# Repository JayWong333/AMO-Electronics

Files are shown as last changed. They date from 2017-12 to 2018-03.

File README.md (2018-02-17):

# AMO-Electronics
Collection of electronics projects intended for conducting atomic physics experiments.

## ECDL_CUR_CTRL
This folder contains the schematics and board layout for an ultra-low noise laser diode current controller. It builds upon proven designs of Libbrecht & Hall (https://doi.org/10.1063/1.1143949) as well as Erickson et. al. (https://doi.org/10.1063/1.2953597).

## Analog Temp Controller
This folder contains the schematics and board layout for a thermoelectric cooler controller. It features a PID-loop that drives a Peltier element (or alternatively a resistive heater) in order to match the resistance of a NTC thermistor to a given set temperature.

## Pfeiffer Compact Gauge Controller
A small standalone board which can be used to interface the Pfeiffer PKR/IKR series compact vacuum gauges. Features an ATMEGA32U4 microcontroller to convert the measurement signal to a pressure and provide it via the built-in USB interface or a I2C/SPI display. The accompanying firmware (in form of an Arduino sketch) can be found in the FW folder.

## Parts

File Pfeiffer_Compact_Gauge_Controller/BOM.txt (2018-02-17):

Partlist exported from C:/Users/alexi/OneDrive/MOTATHOME/780nm Laser Source/AMO-Electronics/Pfeiffer_Compact_Gauge_Controller/Pfeiffer_Compact_Gauge_Controller.sch at 1/28/2018 9:25 PM

Qty Value              Device                                       Package                  Parts                              Description                          CASE MONTHLY_USAGE MPN           OC_FARNELL OC_NEWARK PACKAGE PART_NUMBER                  PRICE PROD_ID    SF_SKU    SPICEPREFIX SUPPLIER               TYPE       VALUE             
1                      DB9MALE                                      DB9_MALE                 J1                                 DB9 Connector                                                                                                                         CONN-09904                                                                           
1                      KX-7                                         3.2X2.5_KX-7             X1                                 Quartz Crystals (MHz) SMD:                                                                                                                                                                                                 
1                      LEDCHIPLED_0805                              CHIPLED_0805             5V                                 LED                                                                                                                                                                                                                        
1                      PINHD-1X2                                    1X02                     JP7                                PIN HEADER                                                                                                                                                                                                                 
1                      PINHD-1X2/90                                 1X02/90                  JP1                                PIN HEADER                                                                                                                                                                                                                 
3                      PINHD-2X2                                    2X02                     JP2, JP4, JP5                      PIN HEADER                                                                                                                                                                                                                 
1                      PINHD-2X3                                    2X03                     JP6                                PIN HEADER                                                                                                                                                                                                                 
1                      PINHD-2X4                                    2X04                     JP3                                PIN HEADER                                                                                                                                                                                                                 
1                      USBMINIB                                     USB-MINIB                USB                                USB Connectors                                                                                                                                                                                                             
6   0.1uF              C-EUC0805                                    C0805                    C5, C6, C7, C8, C9, C10            CAPACITOR, European symbol                                                                                                                                 C                                                               
1   0R                 R-US_R0805                                   R0805                    R9                                 RESISTOR, American symbol                                                                                                                                  R                                                               
1   100K               R-US_R0805                                   R0805                    R1                                 RESISTOR, American symbol                                                                                                                                  R                                                               
1   100nF              C-EUC0805                                    C0805                    C12                                CAPACITOR, European symbol                                                                                                                                 C                                                               
8   10K                R-US_R0805                                   R0805                    R2, R5, R6, R8, R10, R11, R12, R59 RESISTOR, American symbol                                                                                                                                  R                                                               
1   10nF               C-EUC0805                                    C0805                    C14                                CAPACITOR, European symbol                                                                                                                                 C                                                               
3   10uF               C-EUC0805                                    C0805                    C15, C16, C17                      CAPACITOR, European symbol                                                                                                                                 C                                                               
1   11K                R-US_R0805                                   R0805                    R7                                 RESISTOR, American symbol                                                                                                                                  R                                                               
1   1A/40V/500mV       DIODE-SCHOTTKY-SS14                          SMA-DIODE                D1                                 Schottky diode                                                                                                                        DIO-08053                                                          1A/40V/500mV      
3   1uF                C-EUC0805                                    C0805                    C3, C4, C11                        CAPACITOR, European symbol                                                                                                                                 C                                                               
2   22R                R-US_R0805                                   R0805                    R3, R4                             RESISTOR, American symbol                                                                                                                                  R                                                               
2   22pF               C-EUC0805                                    C0805                    C1, C2                             CAPACITOR, European symbol                                                                                                                                 C                                                               
1   22uF               CP_SV-C                                      CSV-C                    C13                                POLARIZED CAP                                                                                                                                                                                                              
1   2K                 R-US_R0805                                   R0805                    R13                                RESISTOR, American symbol                                                                                                                                  R                                                               
1   ATMEGA32U4-AU      ATMEGA32U4-AU                                TQFP44                   U1                                 http://www.ladyada.net/library/eagle                                                                                                                                                                                       
1   LM340A             LM1117IMP-5.0                                SOT230P696X180-4N        U6                                 IC REG LDO 800MA 5.0V                                   LM1117IMP-5.0 -          41K3451   SOT-223                                                                     National Semiconductor                              
1   MF-MSMF050-2 500mA PROTEZIONE_0002_MF-MSMF050-2                 PROTEZIONE_L1812         F1                                 500 mA Multifuse ? Polyfuse               _____                                                    MF-MSMF050-2                 _____                                  _____                  Protezione MF-MSMF050-2 500mA
1   MH2029-300Y        PROTEZIONE_0001_BLM21PG300SN1D_/_MH2029-300Y PROTEZIONE_0805          L4                                 BLM21                                     _____                                                    BLM21PG300SN1D_/_MH2029-300Y _____                                  _____                  Protezione MH2029-300Y       
1   MOM SWITCH         MOMENTARY-SWITCH-SPST-SMD-5.2MM              TACTILE_SWITCH_SMD_5.2MM S1                                 Momentary Switch (Pushbutton) - SPST                                                                                                  SWCH-08247 COM-08720                                                                 
4   MOUNT-PAD-ROUND2.8 MOUNT-PAD-ROUND2.8                           2,8-PAD                  H1, H2, H3, H4                     MOUNTING PAD, round                                                                                                                                                                                                        
1   OPEN               R-US_R0805                                   R0805                    R14                                RESISTOR, American symbol                                                                                                                                  R                                                               
1   TL072D             TL072D                                       SO08                     IC1                                OP AMP

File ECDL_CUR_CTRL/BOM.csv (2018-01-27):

Qty | Value | Device | Package | Got
2 |  | LEDCHIPLED_0805 | CHIPLED_0805 | x
1 |  | MMBT2907ALT1-PNP-SOT23-BEC | SOT23-BEC | x
3 |  | PINHD-1X2 | 1X02 | o
1 |  | PINHD-1X2/90 | 1X02/90 | o
1 |  | PINHD-1X3 | 1X03 | o
1 |  | PINHD-1X3/90 | 1X03/90 | o
1 |  | PINHD-1X5 | 1X05 | o
1 |  | PINHD-2X3 | 2X03 | o
1 |  | PINHD-2X4 | 2X04 | o
3 |  | SMACONNECTOR | SMA90_DIP | x
4 |  | TEST-POINT2 | PAD.02X.02 | x
1 |  | USBMINIB | USB-MINIB | x
1 | .01uF | C-EUC0805 | C0805 | x
2 | 0.1uF | C-EUC0805 | C0805 | x
3 | 0R | R-US_R0805 | R0805 | x
1 | 1.5R | R-US_R2512 | R2512 | x
5 | 100K | R-US_R0805 | R0805 | x
1 | 100R | R-US_R0805 | R0805 | x
2 | 100R | R-US_R2512 | R2512 | x
22 | 100nF | C-EUC0805 | C0805 | x
1 | 100uH | CD54 | CD54 | o
38 | 10K | R-US_R0805 | R0805 | x
3 | 10nF | C-EUC0805 | C0805 | x
16 | 10uF | C-EUC0805 | C0805 | x
1 | 11K | R-US_R0805 | R0805 | x
8 | 1K | R-US_R0805 | R0805 | x
2 | 1N4001 | MBRA340T3 | SMA | x
6 | 1uF | C-EUC0805 | C0805 | x
2 | 220uF | CP_SV-D | CSV-D | x
1 | 22uF | C-EUC0805 | C0805 | x
2 | 22uF | CP_SV-C | CSV-C | x
1 | 240R | R-US_R0805 | R0805 | x
1 | 28.7K | R-US_R0805 | R0805 | x
3 | 2K | R-US_R0805 | R0805 | x
1 | 2N7002 | SMD-MOSFET-N-CH-60V-300MA-LOGIC-LEVEL-FET-2N7002(SOT-23) | SOT-23 | x
1 | 32.768Khz_SMD | CRISTALLI_0213_ABS07-32.768KHZ-T | EPSON_FC_145 | x
2 | 330R | R-US_R0805 | R0805 | x
1 | 33nF | C-EUC0805 | C0805 | x
1 | 3A/40V/500mV | DIODE-SCHOTTKY-B340A | SMA-DIODE | x
2 | 3K | R-US_R0805 | R0805 | x
2 | 47uF | CP_3528-21R | C3528-21R/T | x
1 | 50K | R-US_R0805 | R0805 | x
1 | 50R | R-US_R0805 | R0805 | x
1 | 50R or 0R | R-US_R0805 | R0805 | x
1 | 5K | R-TRIMM3296W | RTRIM3296W | x
1 | 7.5K | R-US_R0805 | R0805 | x
1 | 74LVC1G125DCKR | SN74LVC1G125DCKR | SC70-5 | x
1 | AD5541 | AD5541 | SOIC-8 | x
2 | AD8676 | AD8676 | SO8 | x
1 | ATSAMD21G-A | ATSAMD21G-A | TQFP-48 |  | <<
2 | BRNCG0603MLC-05E | BRNCG0603MLC-05E | CT/CN0603 | x
2 | CD54 | CD54 | CD54 | x
1 | ENBL | PINHD-1X2 | 1X02 | o
1 | EN_LED | PINHD-1X2 | 1X02 | o
1 | IRF9Z14 | IRF9530 | TO220BV | x
1 | L7912 | L7912 | TO223-3 | x
1 | LM1117IMP-3.3 | LM1117IMP-3.3 | SOT230P696X180-4N | x
1 | LM1117IMP-5.0 | LM1117IMP-5.0 | SOT230P696X180-4N | x
1 | LM317MDT | LM317MDT | DPACK | x
1 | LM340S-12 | LM340S-12 | TO263-3 | x
1 | LM399H | LM399H | TO39/4 | x
1 | MF-MSMF050-2 500mA | MF-MSMF050-2 | L1812 | x
1 | MH2029-300Y | BLM21PG300SN1D_/_MH2029-300Y | 805 | x
1 | MOM SWITCH | MOMENTARY-SWITCH-SPST-SMD-5.2MM | SWITCH_SMD_5.2MM | x
1 | OPA2227D | OPA2227D | SO08 |  | <<
1 | PMV48XP | TRANSISTORS_0297_PMV48XP | TRANSISTORS_SOT-23 | x
1 | SSM3J328R.LF | SMD-MOSFET-P-CH-20V-6A-SSM3J328R(SOT-23) | SOT-23 | x
1 | TL071D | TL071D | SO08 | x
1 | TS514AID | TS514AID | SOIC127P600X175-14N | x

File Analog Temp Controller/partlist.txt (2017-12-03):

Partlist

Exported from ECDL_CUR_CTRL.brd at 9/26/2017 2:15 PM

EAGLE Version 8.3.1 Copyright (c) 1988-2017 Autodesk, Inc.

Assembly variant: 

Part     Value          Package            Library                                Position (mil)        Orientation

C11      C_SNUB         C0603              rcl                                    (2050 530)            R270
R9       R_SNUB         R0603              rcl                                    (2050 400)            R90

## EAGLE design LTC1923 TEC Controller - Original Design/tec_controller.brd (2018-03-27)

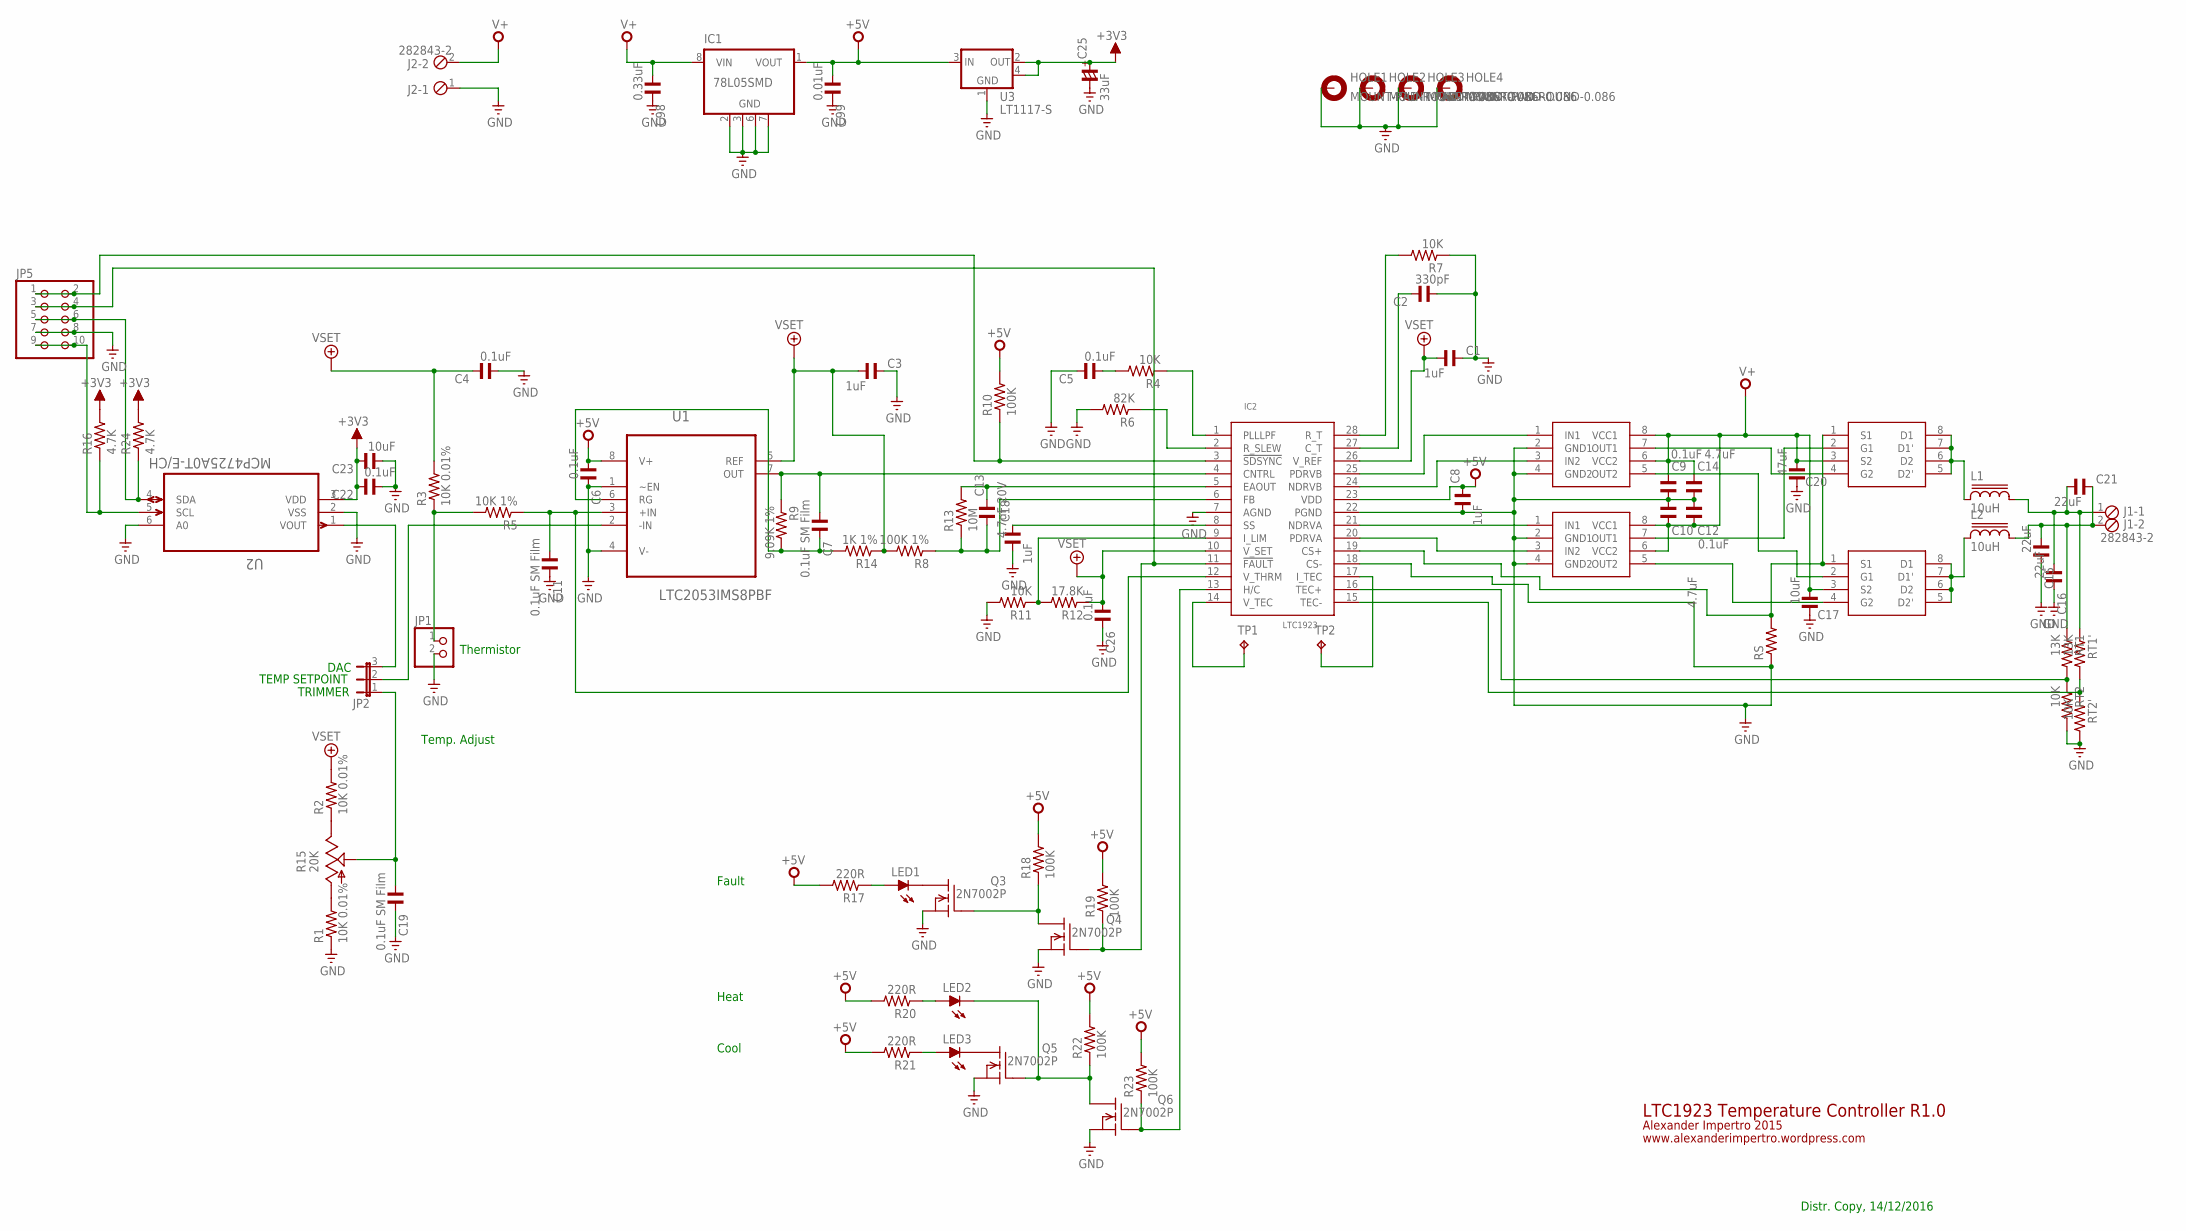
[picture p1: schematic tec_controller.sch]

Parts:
C1, C3, C8, C18: 1uF; C0603
C2: 330pF; C0603
C4, C5, C6, C9, C12, C22, C26: 0.1uF; C0603
C7, C11, C19: 0.1uF SM Film; C0805
C10, C14: 4.7uF; C0603
C13: 4.7uF 20V; C1206
C15, C16, C21: 22uF; C0603
C17, C23: 10uF; C0603
C20: 47uF; C0805
C25: 33uF; 153CLV-0505
C98: 0.33uF; C0805
C99: 0.01uF; C0805
HOLE1, HOLE2, HOLE3, HOLE4: MOUNT-PAD-ROUND-0.086; 086-PAD
IC1: 78L05SMD; SO08
IC2: LTC1923; SSOP28
IC3, IC4: LTC1693-1; SO-08
IC5, IC6: IRF7343; SO-08
J1, J2: 282843-2
JP1: PINHD-1X2; 1X02
JP2: JP2E; JP2
JP5: PINHD-2X5; 2X05
L1, L2: 10uH; DRA127
LED1, LED2, LED3: LEDCHIPLED_0805; CHIPLED_0805
Q3, Q4, Q5, Q6: 2N7002P; SOT95P230X110-3N
R1, R2, R3: 10K 0.01%; R0603
R4, R7, R11: 10K; R0603
R5: 10K 1%; R0603
R6: 82K; R0603
R8: 100K 1%; R0603
R9: 9.09K 1%; R0603
R10: 100K; R0805
R12: 17.8K; R0805
R13: 10M; R0805
R14: 1K 1%; R0603
R15: 20K; B25P
R16, R24: 4.7K; R0603
R17, R20, R21: 220R; R0603
R18, R19, R22, R23: 100K; R0603
RS: R-EU_R2512; R2512
RT1, RT1': 13K; R0603
RT2, RT2': 10K; R0603
TP1, TP2: TPTP10SQ; TP10SQ
U1: LTC2053IMS8PBF; SOP65P490X110-8N
U2: MCP4725A0T-E/CH; SOT95P270X145-6N
U3: LT1117-S; SOT223

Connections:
+3V3: C22.1, C23.1, C25.+, R16.2, R24.2, U2.3 (VDD), U3.2 (OUT), U3.4 (TAB)
+5V: C6.2, C8.1, C99.2, IC1.1 (VOUT), IC2.23 (VDD), R10.2, R17.2, R18.2, R19.2, R20.2, R21.2, R22.2, R23.2, U1.8 (V+), U3.3 (IN)
+5V/2: C1.2, C3.2, C4.1, C26.2, IC2.10 (V_SET), IC2.26 (V_REF), R2.2, R3.2, R8.2, R12.1, R14.1, U1.5 (REF)
GND: C1.1, C2.2, C3.1, C4.2, C5.1, C6.1, C8.2, C9.1, C10.2, C11.1, C12.2, C14.1, C15.1, C16.1, C17.1, C18.2, C19.1, C20.1, C22.2, C23.2, C25.-, C26.1, C98.1, C99.1, HOLE1.B086, HOLE2.B086, HOLE3.B086, HOLE4.B086, IC1.2 (GND), IC1.3 (GND), IC1.6 (GND), IC1.7 (GND), IC2.7 (AGND), IC2.18 (CS-), IC2.22 (PGND), IC3.2 (GND1), IC3.4 (GND2), IC4.2 (GND1), IC4.4 (GND2), J2.1, JP1.2, JP5.7, JP5.8, Q3.2 (S), Q4.2 (S), Q5.2 (S), Q6.2 (S), R1.1, R6.2, R7.1, R11.2, RS.1, RT2.2, RT2'.2, U1.1 (~EN), U1.4 (V-), U2.2 (VSS), U2.6 (A0), U3.1 (GND)
unnamed: LED2.C, Q5.1 (G), Q6.3 (D), R22.1
unnamed: C2.1, IC2.27 (C_T)
unnamed: IC2.14 (V_TEC), TP1.TP
unnamed: IC2.17 (I_TEC), TP2.TP
unnamed: IC2.13 (H/C), Q6.1 (G), R23.1
unnamed: IC2.28 (R_T), R7.2
unnamed: LED3.C, Q5.3 (D)
unnamed: LED2.A, R20.1
unnamed: LED3.A, R21.1
unnamed: IC2.11 (!FAULT), JP5.3, JP5.4, Q4.1 (G), R19.1
unnamed: Q3.1 (G), Q4.3 (D), R18.1
unnamed: LED1.C, Q3.3 (D)
unnamed: LED1.A, R17.1
unnamed: C7.2, IC2.4 (CNTRL), R9.1, U1.7 (OUT)
unnamed: C11.2, IC2.12 (V_THRM), R5.1, U1.3 (+IN)
unnamed: JP1.1, R3.1, R5.2
unnamed: C7.1, R9.2, R14.2, U1.6 (RG)
unnamed: JP2.2, U1.2 (-IN)
unnamed: R1.2, R15.A
unnamed: R2.1, R15.E
unnamed: IC2.9 (I_LIM), R11.1, R12.2
unnamed: IC2.2 (R_SLEW), R6.1
unnamed: JP2.3, U2.1 (VOUT)
unnamed: C18.1, IC2.8 (SS)
unnamed: C5.2, R4.2
unnamed: IC2.1 (PLLLPF), R4.1
unnamed: C13.2, IC2.6 (FB), R8.1, R13.1
unnamed: C13.1, IC2.5 (EAOUT), R13.2
unnamed: C19.2, JP2.1, R15.S
unnamed: IC2.16 (TEC+), RT1.2, RT2.1
unnamed: IC2.25 (PDRVB), IC3.1 (IN1)
unnamed: IC2.24 (NDRVB), IC3.3 (IN2)
unnamed: IC2.21 (NDRVA), IC4.1 (IN1)
unnamed: IC2.20 (PDRVA), IC4.3 (IN2)
unnamed: IC2.15 (TEC-), RT1'.2, RT2'.1
unnamed: IC2.3 (!SDSYNC), JP5.1, JP5.2, R10.1
unnamed: IC2.19 (CS+), IC5.1 (S1), IC6.1 (S1), RS.2
unnamed: IC4.7 (OUT1), IC5.2 (G1)
unnamed: IC3.7 (OUT1), IC5.4 (G2)
unnamed: IC3.5 (OUT2), IC6.2 (G1)
unnamed: C16.2, C21.2, J1.1, L1.2, RT1'.1
unnamed: C15.2, C21.1, J1.2, L2.2, RT1.1
unnamed: IC5.5 (D2'), IC5.6 (D2), IC5.7 (D1'), IC5.8 (D1), L1.1
unnamed: IC6.5 (D2'), IC6.6 (D2), IC6.7 (D1'), IC6.8 (D1), L2.1
unnamed: JP5.5, JP5.6, R24.1, U2.4 (SDA)
unnamed: JP5.9, JP5.10, R16.1, U2.5 (SCL)
unnamed: IC4.5 (OUT2), IC6.4 (G2)
V+: C9.2, C10.1, C12.1, C14.2, C17.2, C20.2, C98.2, IC1.8 (VIN), IC3.6 (VCC2), IC3.8 (VCC1), IC4.6 (VCC2), IC4.8 (VCC1), IC5.3 (S2), IC6.3 (S2), J2.2

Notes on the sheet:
Cool
Heat
Fault
Thermistor
Temp. Adjust
TEMP SETPOINT
DAC
TRIMMER
Alexander Impertro 2015
www.alexanderimpertro.wordpress.com
LTC1923 Temperature Controller R1.0
Distr. Copy, 14/12/2016

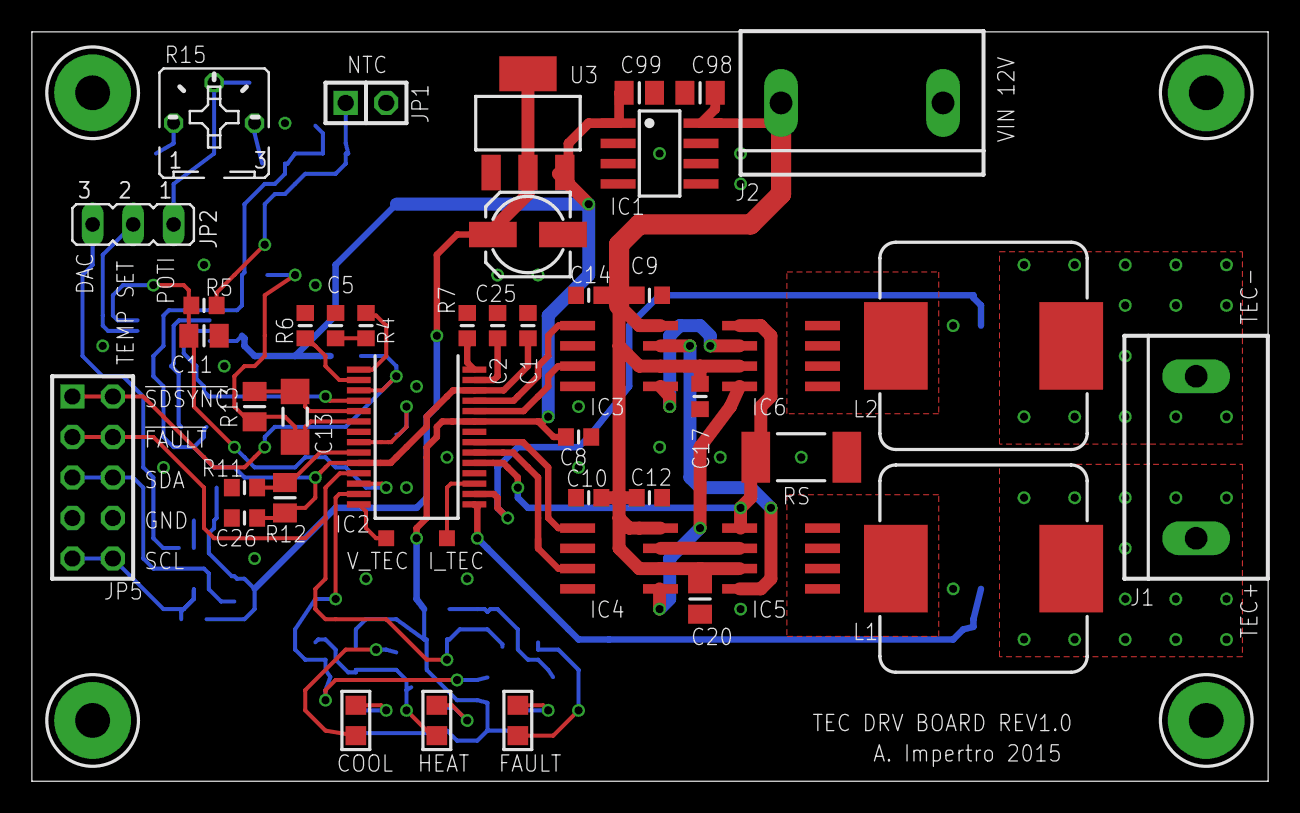
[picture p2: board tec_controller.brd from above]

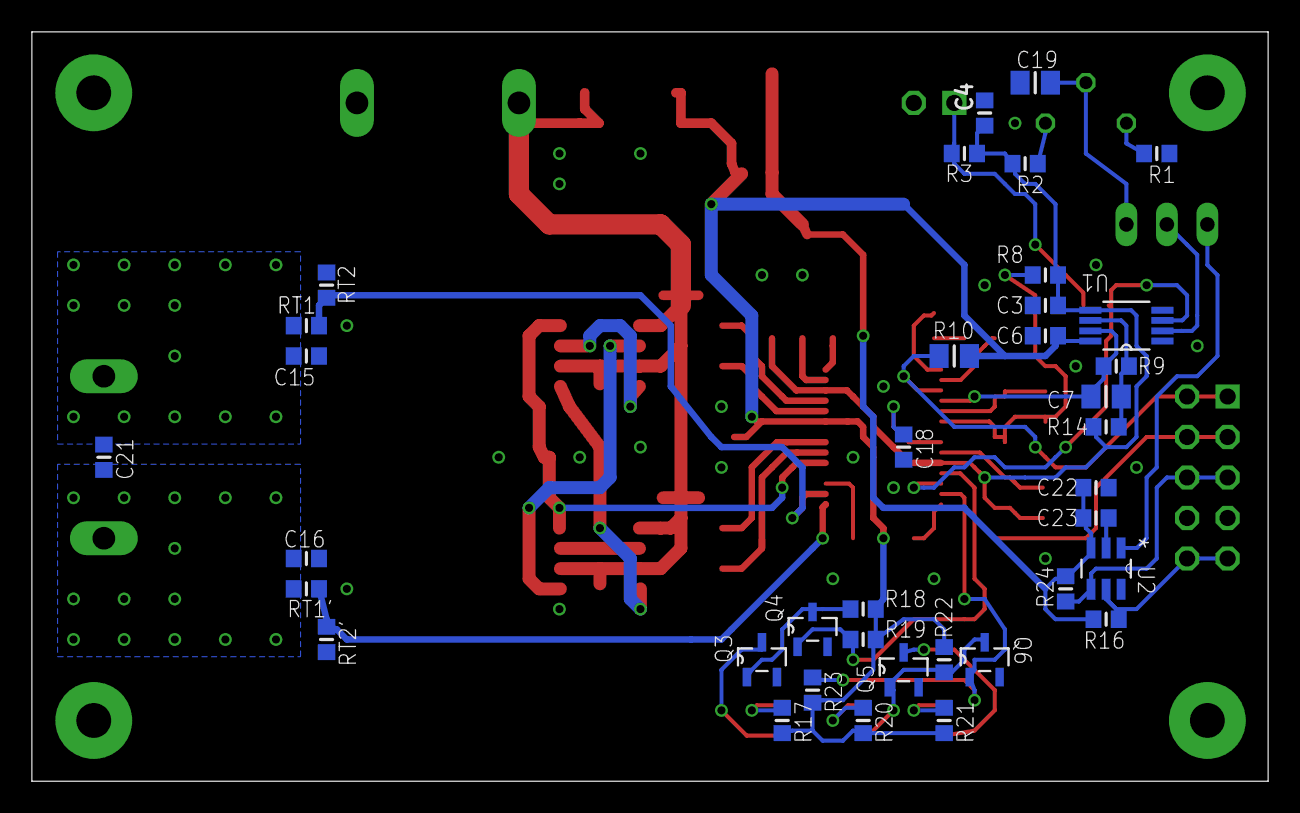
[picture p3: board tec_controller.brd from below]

Board: 2 copper layers, 77.5 x 47.0 mm, 85 parts (37 on the bottom side), 52 nets.

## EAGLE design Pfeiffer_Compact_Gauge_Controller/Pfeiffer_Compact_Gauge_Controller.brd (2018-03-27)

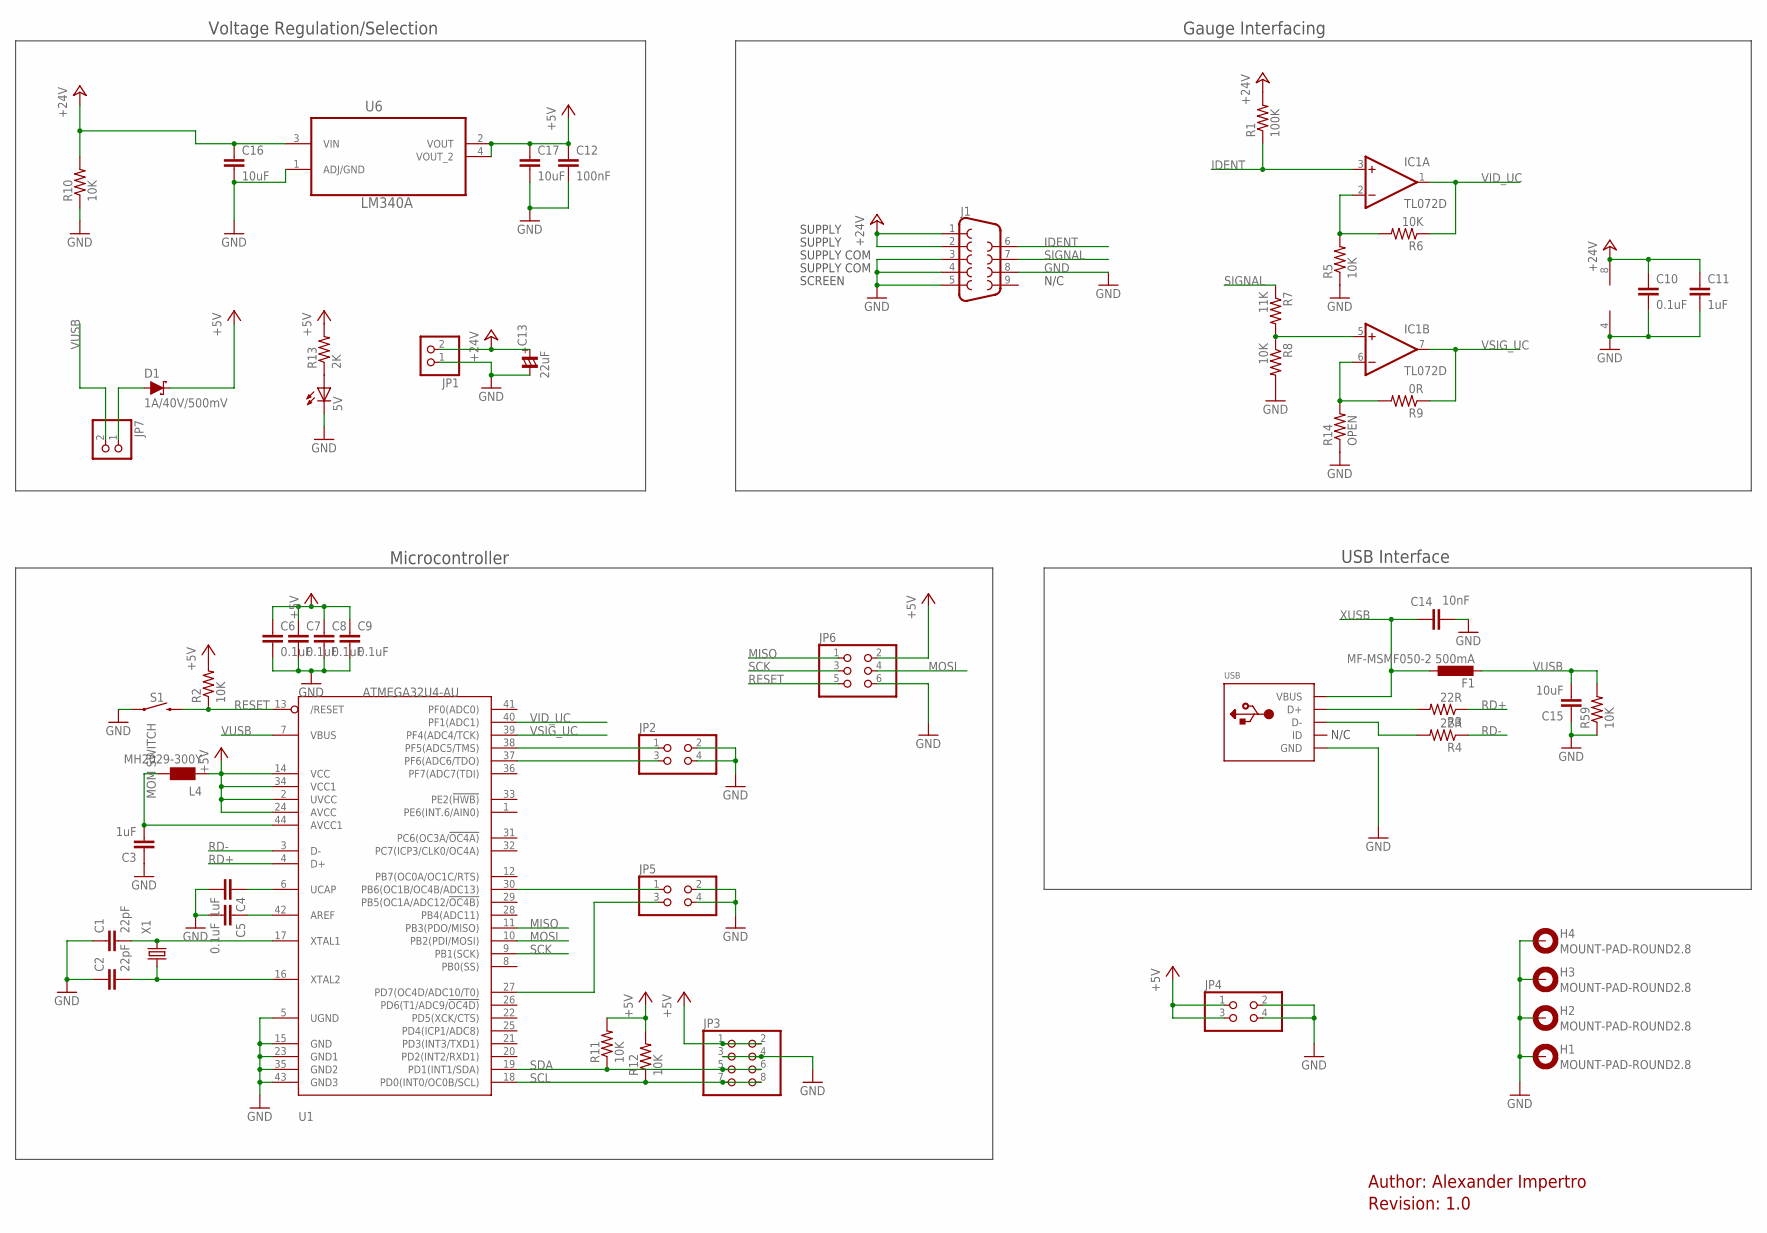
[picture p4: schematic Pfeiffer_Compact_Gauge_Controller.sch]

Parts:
5V: LEDCHIPLED_0805; CHIPLED_0805
C1, C2: 22pF; C0805
C3, C4, C11: 1uF; C0805
C5, C6, C7, C8, C9, C10: 0.1uF; C0805
C12: 100nF; C0805
C13: 22uF; CSV-C
C14: 10nF; C0805
C15, C16, C17: 10uF; C0805
D1: 1A/40V/500mV; SMA-DIODE
F1: MF-MSMF050-2 500mA; PROTEZIONE_L1812
H1, H2, H3, H4: MOUNT-PAD-ROUND2.8; 2,8-PAD
IC1: TL072D; SO08
J1: DB9MALE; DB9_MALE
JP1: PINHD-1X2/90; 1X02/90
JP2, JP4, JP5: PINHD-2X2; 2X02
JP3: PINHD-2X4; 2X04
JP6: PINHD-2X3; 2X03
JP7: PINHD-1X2; 1X02
L4: MH2029-300Y; PROTEZIONE_0805
R1: 100K; R0805
R2, R5, R6, R8, R10, R11, R12, R59: 10K; R0805
R3, R4: 22R; R0805
R7: 11K; R0805
R9: 0R; R0805
R13: 2K; R0805
R14: OPEN; R0805
S1: MOM SWITCH; TACTILE_SWITCH_SMD_5.2MM
U1: ATMEGA32U4-AU; TQFP44
U6: LM340A; SOT230P696X180-4N
USB: USBMINIB; USB-MINIB
X1: KX-7; 3.2X2.5_KX-7

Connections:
+5V: C6.1, C7.1, C8.1, C9.1, C12.1, C17.1, D1.C, JP3.1, JP3.2, JP4.1, JP4.3, JP6.2, L4.1, R2.2, R11.2, R12.2, R13.2, U1.2 (UVCC), U1.14 (VCC), U1.24 (AVCC), U1.34 (VCC1), U6.2 (VOUT), U6.4 (VOUT_2)
+24V: C10.1, C11.1, C13.+, C16.1, IC1.8 (V+), J1.1, J1.2, JP1.2, R1.2, R10.2, U6.3 (VIN)
GND: 5V.C, C1.1, C2.1, C3.1, C4.2, C5.2, C6.2, C7.2, C8.2, C9.2, C10.2, C11.2, C12.2, C13.-, C14.2, C15.1, C16.2, C17.2, H1.B2,8, H2.B2,8, H3.B2,8, H4.B2,8, IC1.4 (V-), J1.3, J1.4, J1.5, J1.8, JP1.1, JP2.2, JP2.4, JP3.3, JP3.4, JP4.2, JP4.4, JP5.2, JP5.4, JP6.6, R5.1, R8.2, R10.1, R14.1, R59.1, S1.1, U1.5 (UGND), U1.15 (GND), U1.23 (GND1), U1.35 (GND2), U1.43 (GND3), U6.1 (ADJ/GND), USB.GND
IDENT: IC1.3 (+IN), J1.6, R1.1
MISO: JP6.1, U1.11 (PB3(PDO/MISO))
MOSI: JP6.4, U1.10 (PB2(PDI/MOSI))
unnamed: C1.2, U1.17 (XTAL1), X1.3 (2)
unnamed: C2.2, U1.16 (XTAL2), X1.1
unnamed: C3.2, L4.2, U1.44 (AVCC1)
unnamed: C4.1, U1.6 (UCAP)
unnamed: C5.1, U1.42 (AREF)
unnamed: R3.2, USB.D+
unnamed: R4.2, USB.D-
unnamed: IC1.2 (-IN), R5.2, R6.2
unnamed: IC1.6 (-IN), R9.2, R14.2
unnamed: IC1.5 (+IN), R7.2, R8.1
unnamed: JP2.1, U1.38 (PF5(ADC5/TMS))
unnamed: D1.A, JP7.1
unnamed: JP2.3, U1.37 (PF6(ADC6/TDO))
unnamed: JP5.1, U1.30 (PB6(OC1B/OC4B/ADC13))
unnamed: JP5.3, U1.27 (PD7(OC4D/ADC10/T0))
unnamed: 5V.A, R13.1
RD+: R3.1, U1.4 (D+)
RD-: R4.1, U1.3 (D-)
RESET: JP6.5, R2.1, S1.3 (2), U1.13 (/RESET)
SCK: JP6.3, U1.9 (PB1(SCK))
SCL: JP3.7, JP3.8, R12.1, U1.18 (PD0(INT0/OC0B/SCL))
SDA: JP3.5, JP3.6, R11.1, U1.19 (PD1(INT1/SDA))
SIGNAL: J1.7, R7.1
VID_UC: IC1.1 (OUT), R6.1, U1.40 (PF1(ADC1))
VSIG_UC: IC1.7 (OUT), R9.1, U1.39 (PF4(ADC4/TCK))
VUSB: C15.2, F1.2, JP7.2, R59.2, U1.7 (VBUS)
XUSB: C14.1, F1.1, USB.VBUS

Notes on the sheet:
SUPPLY
SUPPLY COM
SCREEN
N/C
Author: Alexander Impertro
Revision: 1.0
Voltage Regulation/Selection
Microcontroller
Gauge Interfacing
USB Interface

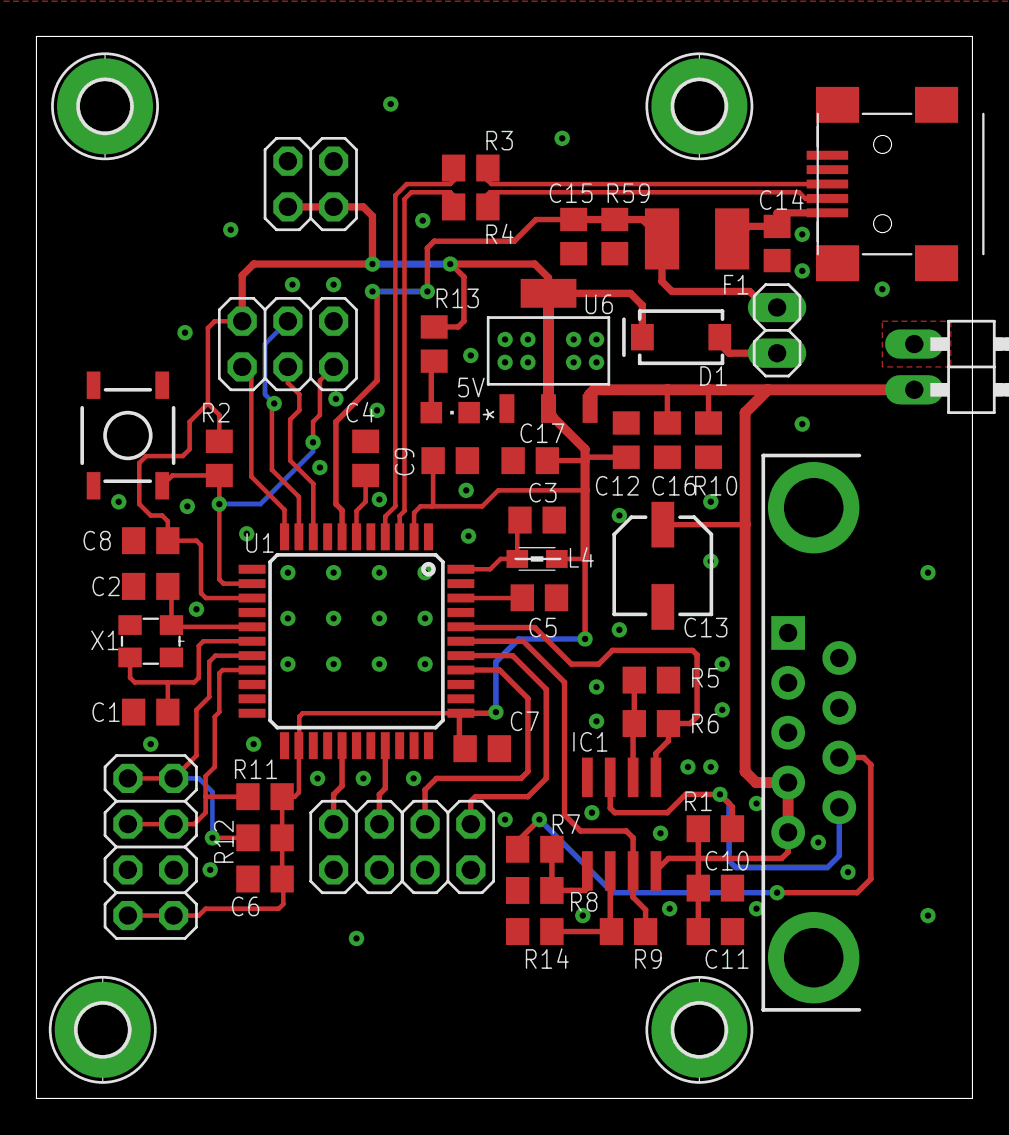
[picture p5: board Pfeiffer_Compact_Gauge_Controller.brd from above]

Board: 2 copper layers, 52.0 x 59.0 mm, 54 parts (0 on the bottom side), 33 nets.

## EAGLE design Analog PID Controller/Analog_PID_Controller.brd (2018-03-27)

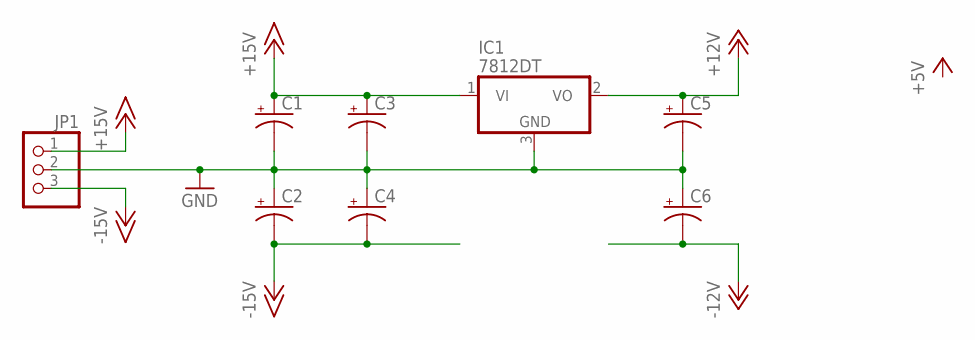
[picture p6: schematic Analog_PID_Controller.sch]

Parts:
C1, C2, C3, C4, C5, C6: CPOL-USD; PANASONIC_D
IC1: 7812DT; TO252
JP1: PINHD-1X3/90; 1X03/90

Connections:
+12V: C5.+, IC1.2 (VO)
+15V: C1.+, C3.+, IC1.1 (VI), JP1.1
-12V: C6.-
-15V: C2.-, C4.-, JP1.3
GND: C1.-, C2.+, C3.-, C4.+, C5.-, C6.+, IC1.3 (GND), JP1.2

Board: 2 copper layers, 8 parts (0 on the bottom side), 4 nets, no tracks yet.

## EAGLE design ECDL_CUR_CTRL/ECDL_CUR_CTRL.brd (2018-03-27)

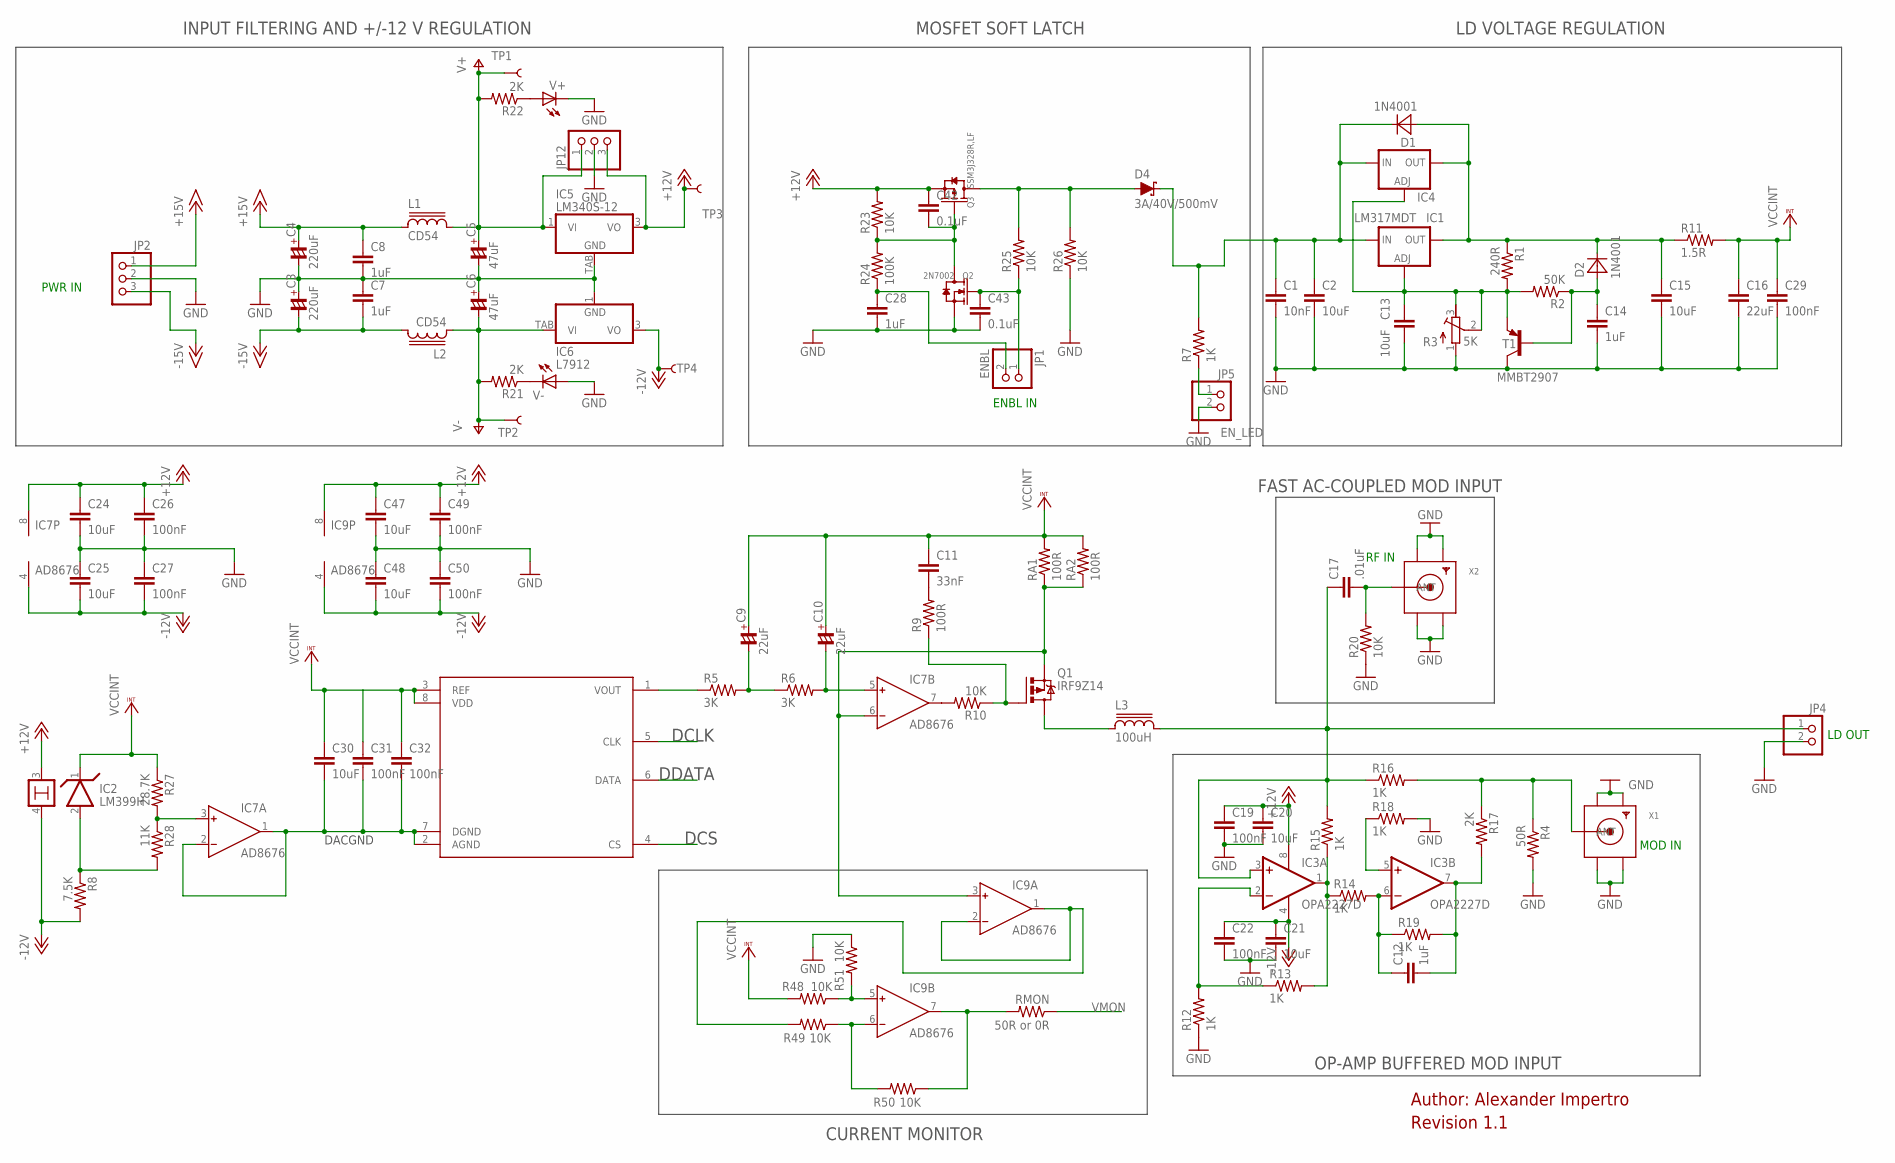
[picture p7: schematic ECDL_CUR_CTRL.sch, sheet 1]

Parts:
C1: 10nF; C0805
C2, C13, C15, C20, C21, C24, C25, C30, C47, C48: 10uF; C0805
C3, C4: 220uF; CSV-D
C5, C6: 47uF; C3528-21R/T
C7, C8, C12, C14, C28: 1uF; C0805
C9, C10: 22uF; CSV-C
C11: 33nF; C0805
C16: 22uF; C0805
C17: .01uF; C0805
C19, C22, C26, C27, C29, C31, C32, C49, C50: 100nF; C0805
C42, C43: 0.1uF; C0805
D1, D2: 1N4001; SMA
D4: 3A/40V/500mV; SMA-DIODE
IC1: LM317MDT; DPACK
IC2: LM399H; TO39/4
IC3: OPA2227D; SO08
IC4: LM317TS; 317TS
IC5: LM340S-12; TO263-3
IC6: L7912; TO223-3
IC7, IC9: AD8676; SO8
JP1: ENBL; 1X02
JP2: PINHD-1X3/90; 1X03/90
JP4: PINHD-1X2/90; 1X02/90
JP5: EN_LED; 1X02
JP12: PINHD-1X3; 1X03
L1, L2: CD54
L3: 100uH; CD54
Q1: IRF9Z14; TO220BV
Q2: 2N7002; SOT-23
Q3: SSM3J328R,LF; SOT-23
R1: 240R; R0805
R2: 50K; R0805
R3: 5K; RTRIM3296W
R4: 50R; R0805
R5, R6: 3K; R0805
R7, R12, R13, R14, R15, R16, R18, R19: 1K; R0805
R8: 7.5K; R0805
R9: 100R; R0805
R10, R20, R23, R25, R26, R48, R49, R50, R51: 10K; R0805
R11: 1.5R; R2512
R17, R21, R22: 2K; R0805
R24: 100K; R0805
R27: 28.7K; R0805
R28: 11K; R0805
RA1, RA2: 100R; R2512
RMON: 50R or 0R; R0805
T1: MMBT2907; SOT23-BEC
TP1, TP2, TP3, TP4: TEST-POINT2; PAD.02X.02
U3: AD5541; SOIC-8
V+: LEDCHIPLED_0805; CHIPLED_0805
V-: LEDCHIPLED_0805; CHIPLED_0805
X1, X2: SMACONNECTOR; SMA90_DIP

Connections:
+12V: C19.1, C20.1, C24.1, C26.1, C42.1, C47.1, C49.1, IC2.3, IC3.8 (V+), IC5.3 (VO), IC7.8 (V+), IC9.8 (V+), JP12.3, Q3.2 (S), R23.2, TP3.P$1; also elsewhere on the board
+15V: C4.+, C8.1, JP2.1, L1.1
-12V: C21.1, C22.1, C25.2, C27.2, C48.2, C50.2, IC2.4, IC3.4 (V-), IC6.3 (VO), IC7.4 (V-), IC9.4 (V-), R8.2, TP4.P$1; also elsewhere on the board
-15V: C3.-, C7.2, JP2.3, L2.2
DACGND: C30.2, C31.2, C32.2, IC7.1 (OUT), IC7.2 (IN-), U3.2 (AGND), U3.7 (DGND); also elsewhere on the board
DCLK: U3.5 (CLK); also elsewhere on the board
DCS: U3.4 (CS); also elsewhere on the board
DDATA: U3.6 (DATA); also elsewhere on the board
GND: C1.2, C2.2, C3.+, C4.-, C5.-, C6.+, C7.1, C8.2, C13.2, C14.2, C15.2, C16.2, C19.2, C20.2, C21.2, C22.2, C24.2, C25.1, C26.2, C27.1, C28.2, C29.2, C43.2, C47.2, C48.1, C49.2, C50.1, IC5.TAB (GND), IC6.1 (GND), JP2.2, JP4.2, JP5.2, JP12.2, Q2.2 (S), R3.1 (A), R4.2, R12.1, R18.2, R20.1, R26.1, R51.1, T1.C, V+.C, V-.A, X1.GND1, X1.GND2, X1.GND3, X1.GND4, X2.GND1, X2.GND2, X2.GND3, X2.GND4; also elsewhere on the board
unnamed: C13.1, IC1.1 (ADJ), IC4.1 (ADJ), R1.2, R2.2, R3.2 (S), R3.3 (E), T1.E
unnamed: L3.1, Q1.D
unnamed: C14.1, D2.A, R2.1, T1.B
unnamed: C11.2, R9.2
unnamed: R5.1, U3.1 (VOUT)
unnamed: C9.-, R5.2, R6.1
unnamed: C10.-, IC7.5 (IN+), R6.2
unnamed: IC2.2, R8.1, R28.2
unnamed: IC7.7 (OUT), R10.2
unnamed: Q1.G, R9.1, R10.1
unnamed: C43.1, JP1.1, Q2.1 (G), R25.1
unnamed: IC7.6 (IN-), IC9.3 (IN+), Q1.S, RA1.1, RA2.1
unnamed: C12.1, IC3.6 (-IN), R14.2, R19.1
unnamed: IC3.2 (-IN), R12.2, R13.1
unnamed: IC3.1 (OUT), R13.2, R14.1, R15.1
unnamed: C12.2, IC3.7 (OUT), R17.2, R19.2
unnamed: R4.1, R16.2, R17.1, X1.ANTENNA (ANT)
unnamed: IC3.5 (+IN), R18.1
unnamed: C17.2, R20.2, X2.ANTENNA (ANT)
unnamed: R22.1, V+.A
unnamed: R21.1, V-.C
unnamed: C1.1, C2.1, D1.C, D4.C, IC1.3 (IN), IC4.3 (IN), R7.2
unnamed: C28.1, JP1.2, R24.1
unnamed: C15.1, D1.A, D2.C, IC1.4 (OUT), IC4.2 (OUT), R1.1, R11.1
unnamed: C42.2, Q2.3 (D), Q3.1 (G), R23.1, R24.2
unnamed: IC7.3 (IN+), R27.2, R28.1
unnamed: D4.A, Q3.3 (D), R25.2, R26.2
unnamed: C17.1, IC3.3 (+IN), JP4.1, L3.2, R15.2, R16.1
unnamed: JP5.1, R7.1
unnamed: IC9.1 (OUT), IC9.2 (IN-), R49.2
unnamed: IC9.5 (IN+), R48.1, R51.2
unnamed: IC9.6 (IN-), R49.1, R50.2
unnamed: IC9.7 (OUT), R50.1, RMON.2
V+: C5.+, IC5.1 (VI), JP12.1, L1.2, R22.2, TP1.P$1
V-: C6.-, IC6.TAB (VI), L2.1, R21.2, TP2.P$1
VCCINT: C9.+, C10.+, C11.1, C16.1, C29.1, C30.1, C31.1, C32.1, IC2.1, R11.2, R27.1, R48.2, RA1.2, RA2.2, U3.3 (REF), U3.8 (VDD)
VMON: RMON.1; also elsewhere on the board

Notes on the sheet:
MOD IN
LD OUT
RF IN
ENBL IN
PWR IN
Revision 1.1
Author: Alexander Impertro
INPUT FILTERING AND +/-12 V REGULATION
MOSFET SOFT LATCH
LD VOLTAGE REGULATION
DCS
DDATA
DCLK
DACGND
VMON
OP-AMP BUFFERED MOD INPUT
FAST AC-COUPLED MOD INPUT
CURRENT MONITOR

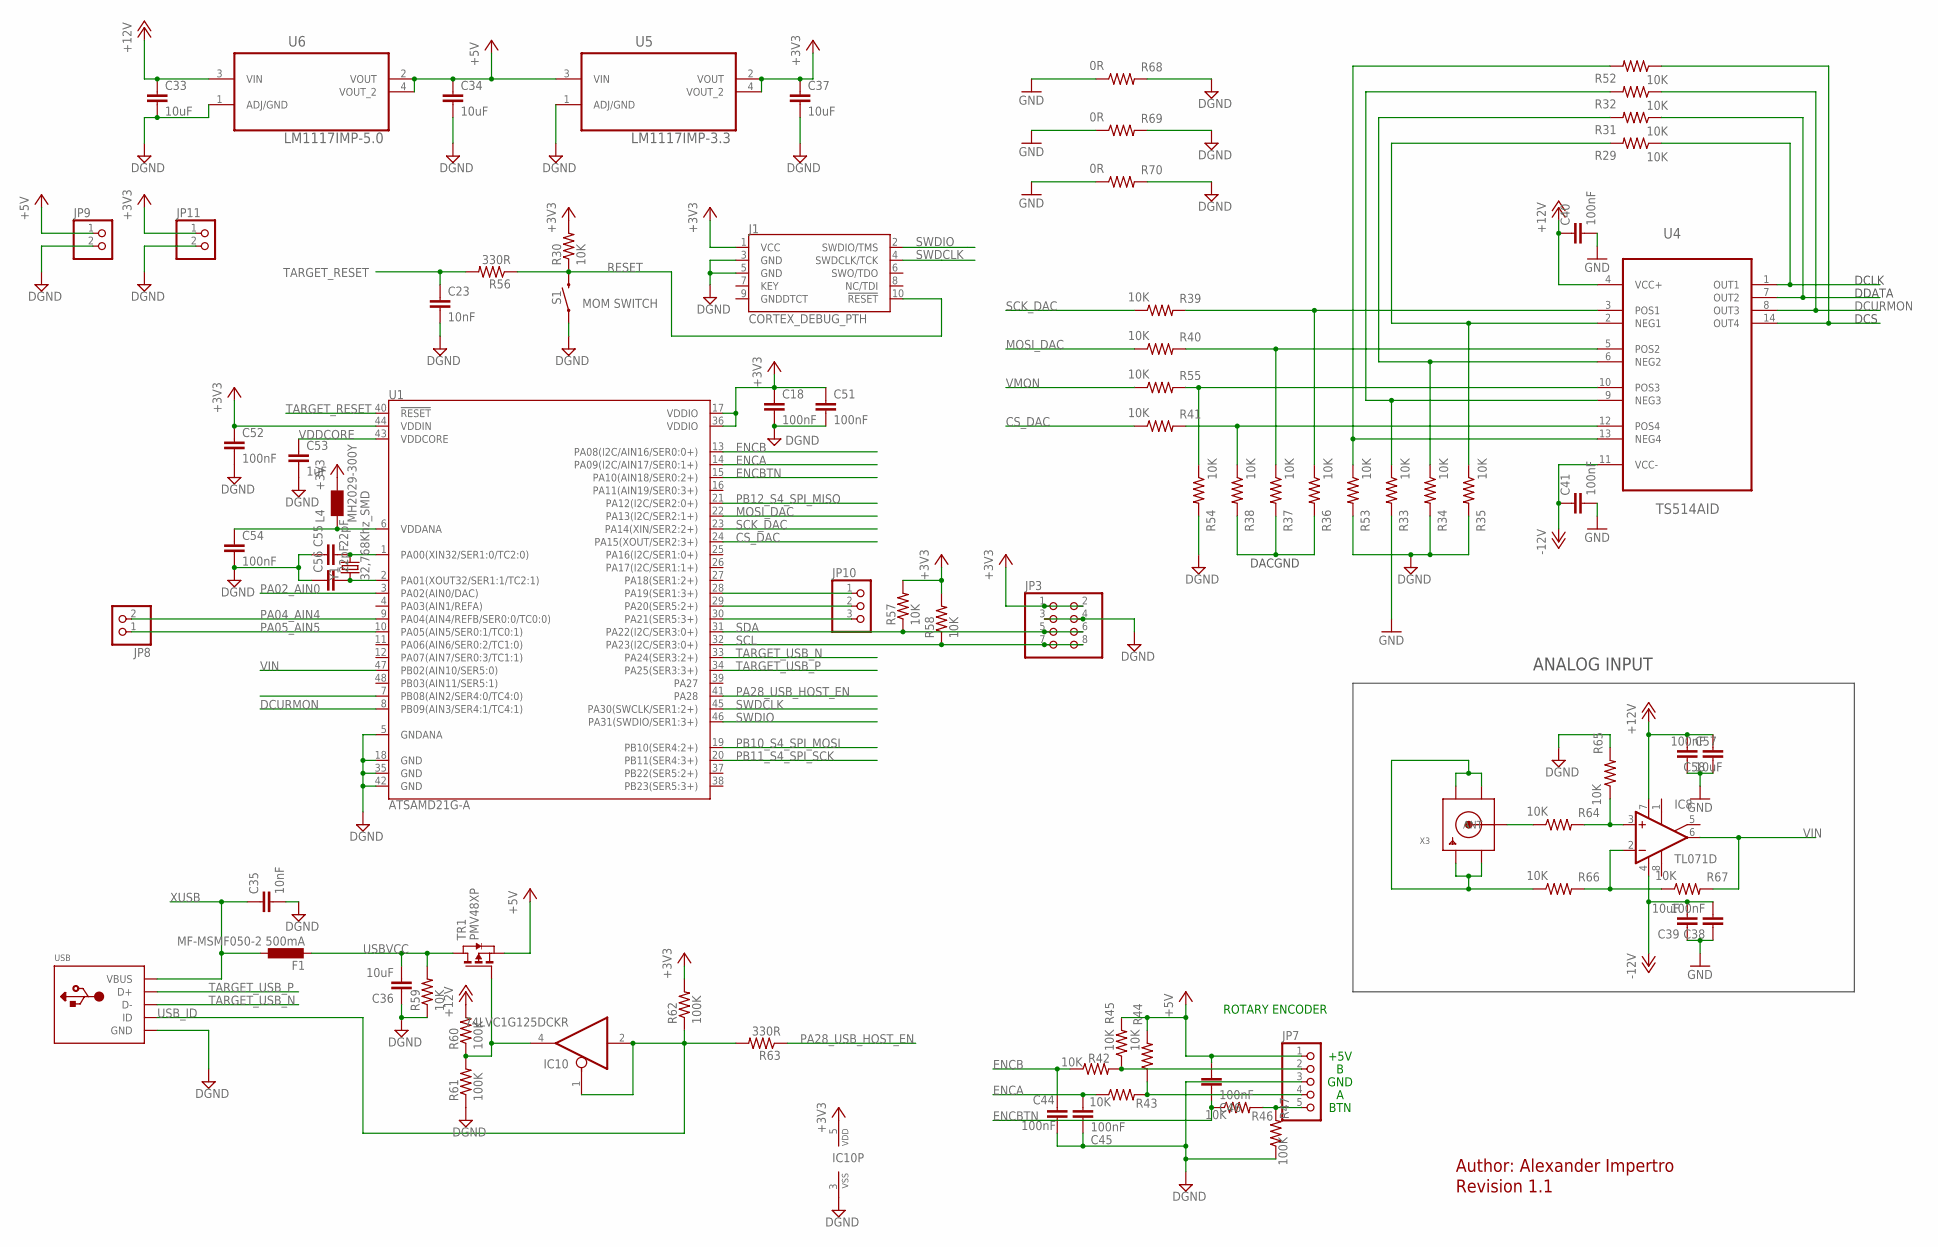
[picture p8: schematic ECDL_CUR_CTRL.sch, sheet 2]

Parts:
C18, C38, C40, C41, C44, C45, C46, C51, C52, C54, C58: 100nF; C0805
C23, C35: 10nF; C0805
C33, C34, C36, C37, C39, C57: 10uF; C0805
C53: 1uF; C0805
C55, C56: 22pF; C0805
F1: MF-MSMF050-2 500mA; PROTEZIONE_L1812
IC8: TL071D; SO08
IC10: 74LVC1G125DCKR; INTEGRATEDCIRCUITS_SC70-5
J1: CORTEX_DEBUG_PTH; 2X5-PTH-1.27MM
JP3: PINHD-2X4; 2X04
JP7: PINHD-1X5; 1X05
JP8, JP9, JP11: PINHD-1X2; 1X02
JP10: PINHD-1X3; 1X03
L4: MH2029-300Y; PROTEZIONE_0805
R29, R30, R31, R32, R33, R34, R35, R36, R37, R38, R39, R40, R41, R42, R43, R44, R45, R46, R52, R53, R54, R55, R57, R58, R59, R64, R65, R66, R67: 10K; R0805
R47, R60, R61, R62: 100K; R0805
R56, R63: 330R; R0805
R68, R69, R70: 0R; R0805
S1: MOM SWITCH; TACTILE_SWITCH_SMD_5.2MM
TR1: PMV48XP; TRANSISTORS_SOT-23
U1: ATSAMD21G-A; TQFP-48
U4: TS514AID; SOIC127P600X175-14N
U5: LM1117IMP-3.3; SOT230P696X180-4N
U6: LM1117IMP-5.0; SOT230P696X180-4N
USB: USBMINIB; USB-MINIB
X3: SMACONNECTOR; SMA90_DIP
Y1: 32,768Khz_SMD; CRISTALLI_RESONATOR_EPSON_FC_145

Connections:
+3V3: C18.1, C37.1, C51.1, C52.1, IC10.5 (VDD), J1.1 (VCC), JP3.1, JP3.2, JP11.1, L4.2, R30.2, R57.2, R58.2, R62.2, U1.17 (VDDIO), U1.36 (VDDIO), U1.44 (VDDIN), U5.2 (VOUT), U5.4 (VOUT_2)
+5V: C34.1, C46.1, JP7.1, JP9.1, R44.2, R45.2, TR1.2 (S), U5.3 (VIN), U6.2 (VOUT), U6.4 (VOUT_2)
+12V: C33.1, C40.1, C57.1, C58.2, IC8.7 (V+), R60.2, U4.4 (VCC+), U6.3 (VIN); also elsewhere on the board
-12V: C38.2, C39.2, C41.1, IC8.4 (V-), U4.11 (VCC-); also elsewhere on the board
CS_DAC: R41.1, U1.24 (PA15(XOUT/SER2:3+))
DACGND: R36.2, R37.2, R38.2; also elsewhere on the board
DCLK: R29.1, U4.1 (OUT1); also elsewhere on the board
DCS: R52.1, U4.14 (OUT4); also elsewhere on the board
DCURMON: R32.1, U1.8 (PB09(AIN3/SER4:1/TC4:1)), U4.8 (OUT3)
DDATA: R31.1, U4.7 (OUT2); also elsewhere on the board
DGND: C18.2, C23.2, C33.2, C34.2, C35.2, C36.1, C37.2, C44.2, C45.2, C51.2, C52.2, C53.2, C54.2, C55.1, C56.1, IC10.3 (VSS), J1.3 (GND), J1.5 (GND), JP3.3, JP3.4, JP7.3, JP9.2, JP11.2, R34.2, R35.2, R47.1, R53.2, R54.2, R59.1, R61.1, R65.2, R68.2, R69.2, R70.2, S1.1, U1.5 (GNDANA), U1.18 (GND), U1.35 (GND), U1.42 (GND), U5.1 (ADJ/GND), U6.1 (ADJ/GND), USB.GND
ENCA: C45.1, R43.1, U1.14 (PA09(I2C/AIN17/SER0:1+))
ENCB: C44.1, R42.1, U1.13 (PA08(I2C/AIN16/SER0:0+))
ENCBTN: C46.2, R46.1, U1.15 (PA10(AIN18/SER0:2+))
GND: C38.1, C39.1, C40.2, C41.2, C57.2, C58.1, R33.2, R68.1, R69.1, R70.1; also elsewhere on the board
MOSI_DAC: R40.1, U1.22 (PA13(I2C/SER2:1+))
unnamed: R29.2, R35.1, U4.2 (NEG1)
unnamed: R36.1, R39.2, U4.3 (POS1)
unnamed: C54.1, L4.1, U1.6 (VDDANA)
unnamed: R31.2, R34.1, U4.6 (NEG2)
unnamed: R66.1, X3.GND1, X3.GND2, X3.GND3, X3.GND4
unnamed: R64.1, X3.ANTENNA (ANT)
unnamed: JP7.2, R42.2, R45.1
unnamed: IC8.3 (+IN), R64.2, R65.1
unnamed: R32.2, R33.1, U4.9 (NEG3)
unnamed: JP7.4, R43.2, R44.1
unnamed: R37.1, R40.2, U4.5 (POS2)
unnamed: R38.1, R41.2, U4.12 (POS4)
unnamed: JP7.5, R46.2, R47.2
unnamed: C55.2, U1.1 (PA00(XIN32/SER1:0/TC2:0)), Y1.P$2 (2)
unnamed: C56.2, U1.2 (PA01(XOUT32/SER1:1/TC2:1)), Y1.P$1 (1)
unnamed: IC10.4 (O), R60.1, R61.2, TR1.3 (G)
unnamed: IC8.2 (-IN), R66.2, R67.1
unnamed: JP10.3, U1.30 (PA21(SER5:3+))
unnamed: JP10.2, U1.29 (PA20(SER5:2+))
unnamed: JP10.1, U1.28 (PA19(SER1:3+))
unnamed: R54.1, R55.2, U4.10 (POS3)
unnamed: R52.2, R53.1, U4.13 (NEG4)
PA02_AIN0: U1.3 (PA02(AIN0/DAC))
PA04_AIN4: JP8.2, U1.9 (PA04(AIN4/REFB/SER0:0/TC0:0))
PA05_AIN5: JP8.1, U1.10 (PA05(AIN5/SER0:1/TC0:1))
PA28_USB_HOST_EN: R63.1, U1.41 (PA28)
PB10_S4_SPI_MOSI: U1.19 (PB10(SER4:2+))
PB11_S4_SPI_SCK: U1.20 (PB11(SER4:3+))
PB12_S4_SPI_MISO: U1.21 (PA12(I2C/SER2:0+))
RESET: J1.10 (!RESET), R30.1, R56.1, S1.3 (2)
SCK_DAC: R39.1, U1.23 (PA14(XIN/SER2:2+))
SCL: JP3.7, JP3.8, R58.1, U1.32 (PA23(I2C/SER3:0+))
SDA: JP3.5, JP3.6, R57.1, U1.31 (PA22(I2C/SER3:0+))
SWDCLK: J1.4 (SWDCLK/TCK), U1.45 (PA30(SWCLK/SER1:2+))
SWDIO: J1.2 (SWDIO/TMS), U1.46 (PA31(SWDIO/SER1:3+))
TARGET_RESET: C23.1, R56.2, U1.40 (!RESET!)
TARGET_USB_N: U1.33 (PA24(SER3:2+)), USB.D-
TARGET_USB_P: U1.34 (PA25(SER3:3+)), USB.D+
USBVCC: C36.2, F1.2, R59.2, TR1.1 (D)
USB_ID: IC10.1 (OE), IC10.2 (I), R62.1, R63.2, USB.ID
VDDCORE: C53.1, U1.43 (VDDCORE)
VIN: IC8.6 (OUT), R67.2, U1.47 (PB02(AIN10/SER5:0))
VMON: R55.1; also elsewhere on the board
XUSB: C35.1, F1.1, USB.VBUS

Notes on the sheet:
DCLK
DACGND
DDATA
DCS
ROTARY ENCODER
+5V
BTN
GND
DCURMON
Author: Alexander Impertro
Revision 1.1
ANALOG INPUT

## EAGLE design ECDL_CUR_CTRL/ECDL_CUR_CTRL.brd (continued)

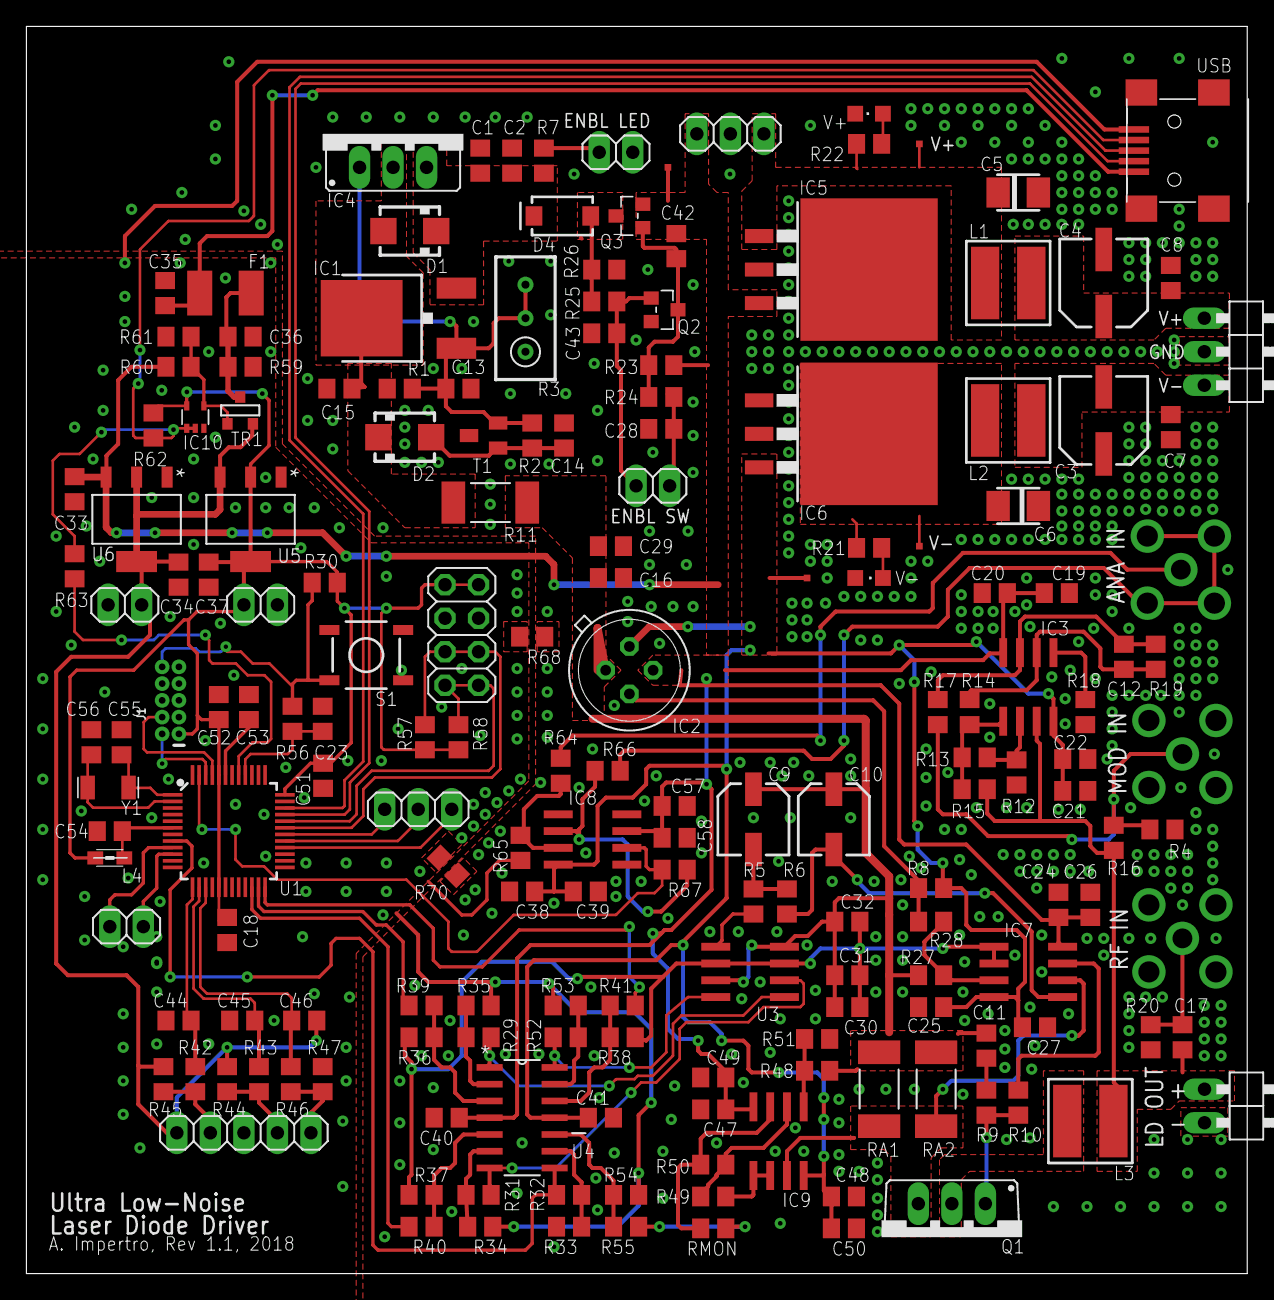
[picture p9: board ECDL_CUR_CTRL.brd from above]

Board: 2 copper layers, 92.5 x 94.5 mm, 183 parts (1 on the bottom side), 94 nets.

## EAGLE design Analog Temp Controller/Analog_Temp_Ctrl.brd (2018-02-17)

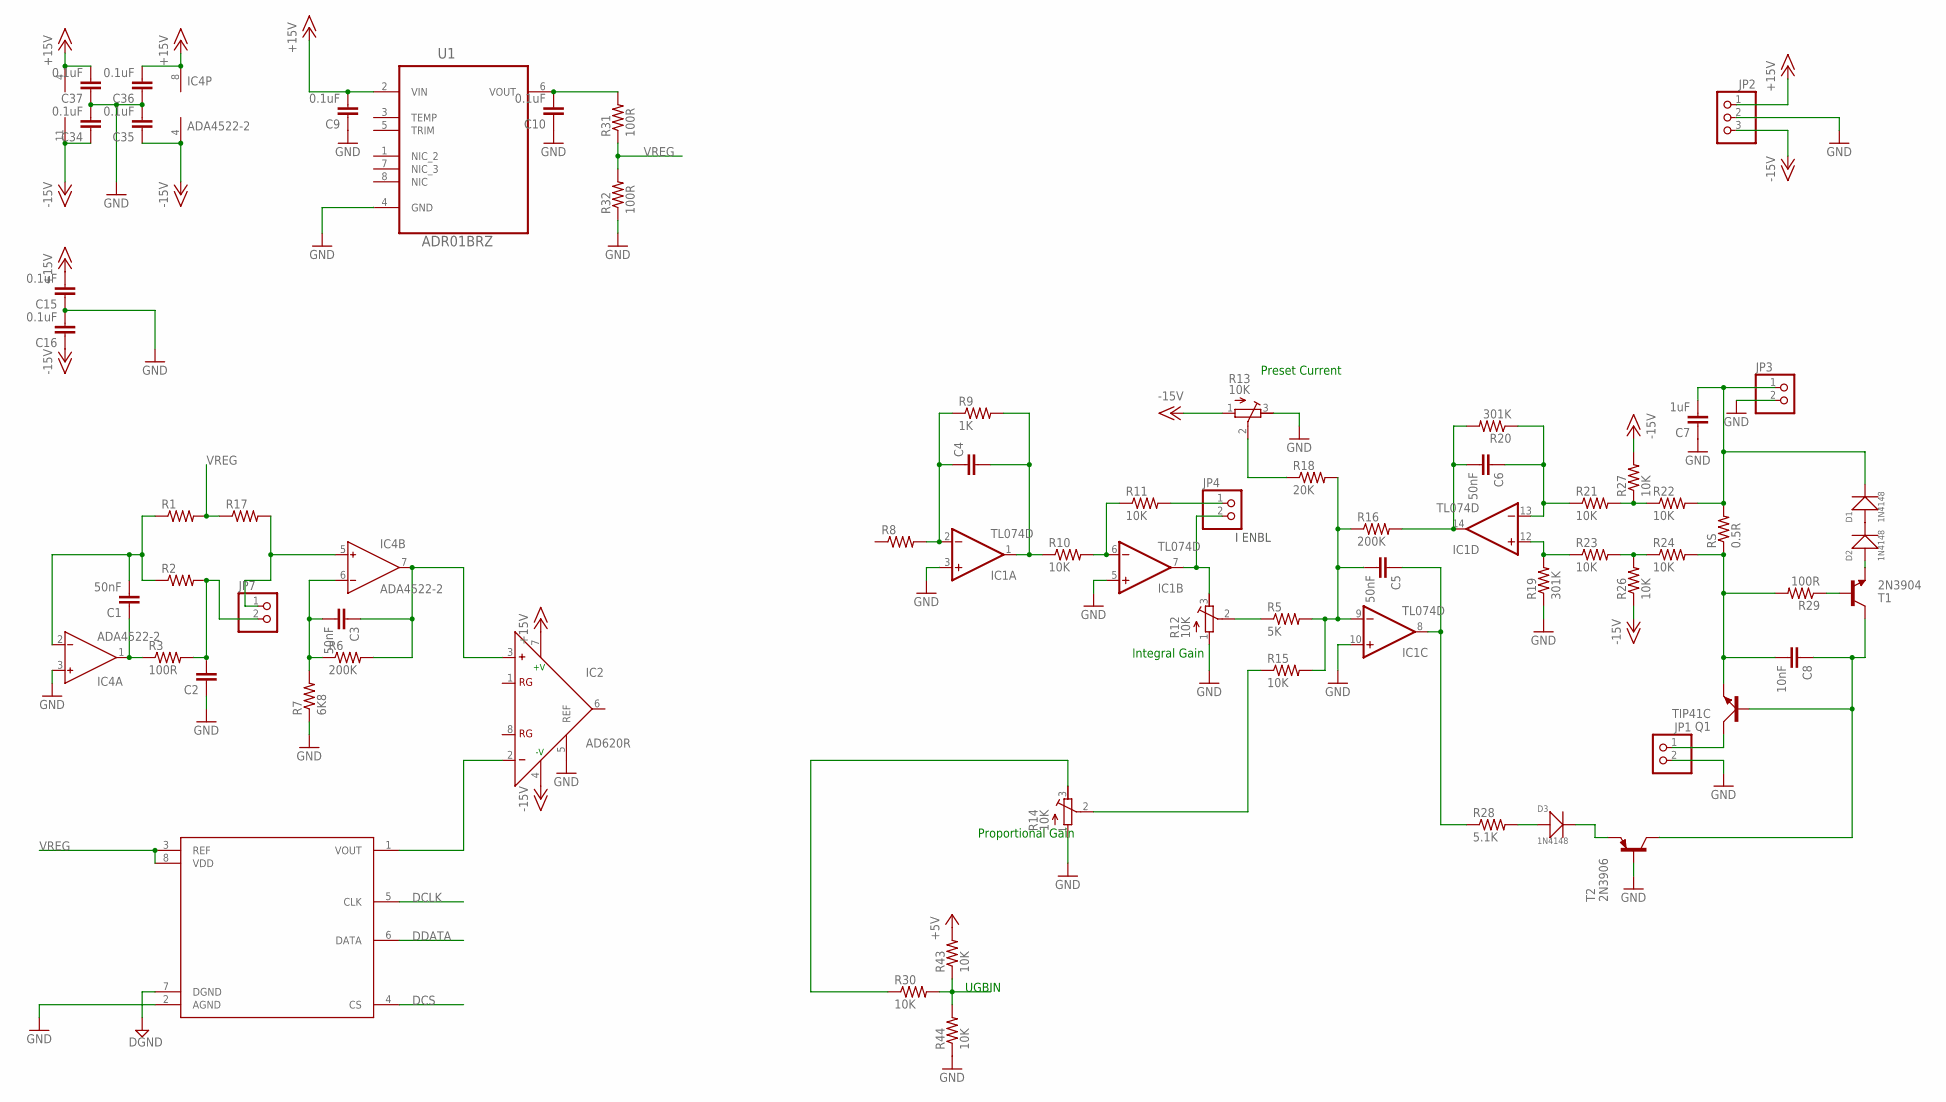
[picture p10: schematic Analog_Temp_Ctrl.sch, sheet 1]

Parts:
C1, C3, C5, C6: 50nF; C0805
C2, C4: C-EUC0805; C0805
C7: 1uF; C0805
C8: 10nF; C0805
C9, C10, C15, C16, C34, C35, C36, C37: 0.1uF; C0805
D1, D2, D3: 1N4148; LL-34
IC1: TL074D; SO14
IC2: AD620R; SO8
IC4: ADA4522-2; SO8
JP1, JP3: PINHD-1X2/90; 1X02/90
JP2: PINHD-1X3/90; 1X03/90
JP4, JP7: PINHD-1X2; 1X02
Q1: TIP41C; TO220AV
R1, R2, R8, R17: R-US_R0805; R0805
R3, R29, R31, R32: 100R; R0805
R5: 5K; R0805
R6, R16: 200K; R0805
R7: 6K8; R0805
R9: 1K; R0805
R10, R11, R15, R21, R22, R23, R24, R26, R27, R30, R43, R44: 10K; R0805
R12, R13, R14: 10K; RTRIM3296W
R18: 20K; R0805
R19, R20: 301K; R0805
R28: 5.1K; R0805
RS: 0.5R; R2512
T1: 2N3904; SOT23-BEC
T2: 2N3906; SOT23-BEC
U1: ADR01BRZ; SOIC127P600X175-8N
U3: AD5541; SOIC-8

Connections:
+5V: R43.2; also elsewhere on the board
+15V: C9.2, C15.2, C36.2, C37.2, IC1.4 (V+), IC2.7 (+V), IC4.8 (V+), JP2.1, U1.2 (VIN); also elsewhere on the board
-15V: C16.1, C34.1, C35.1, IC1.11 (V-), IC2.4 (-V), IC4.4 (V-), JP2.3, R13.1 (A), R26.1, R27.2
DCLK: U3.5 (CLK); also elsewhere on the board
DCS: U3.4 (CS); also elsewhere on the board
DDATA: U3.6 (DATA); also elsewhere on the board
DGND: U3.7 (DGND); also elsewhere on the board
GND: C2.1, C7.1, C9.1, C10.1, C15.1, C16.2, C34.2, C35.2, C36.1, C37.1, IC1.3 (+IN), IC1.5 (+IN), IC1.10 (+IN), IC2.5 (REF), IC4.3 (IN+), JP1.2, JP2.2, JP3.2, R7.1, R12.1 (A), R13.3 (E), R14.1 (A), R19.1, R32.1, R44.1, T2.B, U1.4 (GND), U3.2 (AGND); also elsewhere on the board
unnamed: C1.2, IC4.2 (IN-), R1.1, R2.1
unnamed: JP4.1, R11.2
unnamed: R5.1, R12.2 (S)
unnamed: C1.1, IC4.1 (OUT), R3.1
unnamed: C4.1, IC1.2 (-IN), R8.2, R9.1
unnamed: C2.2, JP7.2, R2.2, R3.2
unnamed: C3.1, IC2.3 (+), IC4.7 (OUT), R6.2
unnamed: R14.2 (S), R15.1
unnamed: C3.2, IC4.6 (IN-), R6.1, R7.2
unnamed: R14.3 (E), R30.1
unnamed: C6.2, IC1.14 (OUT), R16.2, R20.2
unnamed: R13.2 (S), R18.1
unnamed: C5.2, IC1.9 (-IN), R5.2, R15.2, R16.1, R18.2
unnamed: C4.2, IC1.1 (OUT), R9.2, R10.1
unnamed: C5.1, IC1.8 (OUT), R28.1
unnamed: IC1.12 (+IN), R19.2, R23.1
unnamed: R21.2, R22.1, R27.1
unnamed: C6.1, IC1.13 (-IN), R20.1, R21.1
unnamed: IC1.7 (OUT), JP4.2, R12.3 (E)
unnamed: R23.2, R24.1, R26.2
unnamed: C7.2, D1.C (-), JP3.1, R22.2, RS.2
unnamed: C8.2, Q1.E, R24.2, R29.2, RS.1
unnamed: C10.2, R31.2, U1.6 (VOUT)
unnamed: D1.A (+), D2.C (-)
unnamed: D3.A (+), R28.2
unnamed: D3.C (-), T2.E
unnamed: D2.A (+), T1.E
unnamed: R29.1, T1.B
unnamed: C8.1, Q1.B, T1.C, T2.C
unnamed: JP1.1, Q1.C
unnamed: IC1.6 (-IN), R10.2, R11.1
unnamed: IC2.2 (-), U3.1 (VOUT)
RW: IC4.5 (IN+), JP7.1, R17.2
UGBIN: R30.2, R43.1, R44.2; also elsewhere on the board
VREG: R1.2, R17.1, R31.1, R32.2, U3.3 (REF), U3.8 (VDD)

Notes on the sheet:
Integral Gain
Preset Current
Proportional Gain
UGBIN
I ENBL

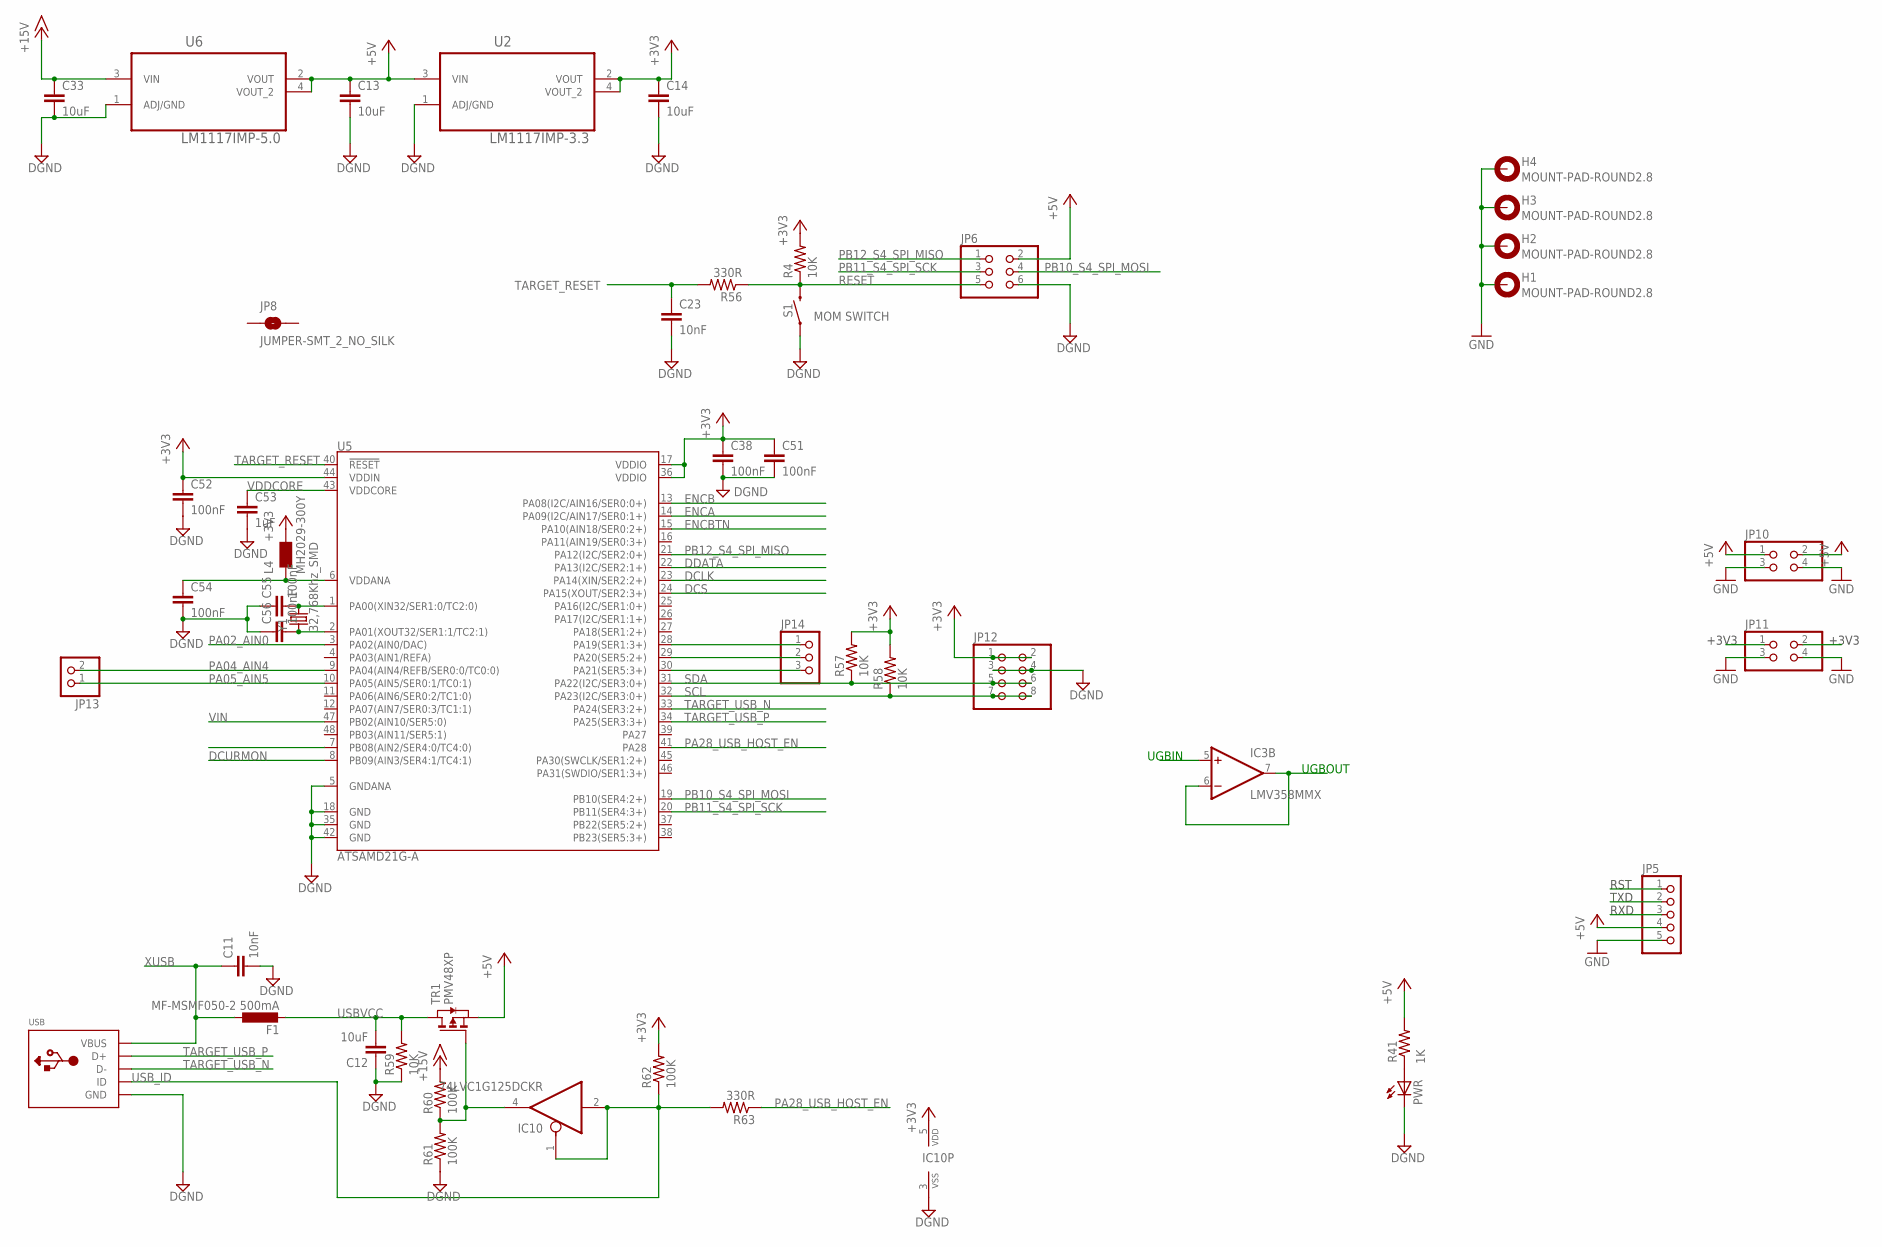
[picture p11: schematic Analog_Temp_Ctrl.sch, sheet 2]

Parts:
C11, C23: 10nF; C0805
C12, C13, C14, C33: 10uF; C0805
C38, C51, C52, C54, C55, C56: 100nF; C0805
C53: 1uF; C0805
F1: MF-MSMF050-2 500mA; PROTEZIONE_L1812
H1, H2, H3, H4: MOUNT-PAD-ROUND2.8; 2,8-PAD
IC3: LMV358MMX; MSOP08
IC10: 74LVC1G125DCKR; INTEGRATEDCIRCUITS_SC70-5
JP5: PINHD-1X5; 1X05
JP6: PINHD-2X3; 2X03
JP8: JUMPER-SMT_2_NO_SILK; SMT-JUMPER_2_NO_SILK
JP10, JP11: PINHD-2X2; 2X02
JP12: PINHD-2X4; 2X04
JP13: PINHD-1X2; 1X02
JP14: PINHD-1X3; 1X03
L4: MH2029-300Y; PROTEZIONE_0805
PWR: LEDCHIPLED_0805; CHIPLED_0805
R4, R57, R58, R59: 10K; R0805
R41: 1K; R0805
R56, R63: 330R; R0805
R60, R61, R62: 100K; R0805
S1: MOM SWITCH; TACTILE_SWITCH_SMD_5.2MM
TR1: PMV48XP; TRANSISTORS_SOT-23
U2: LM1117IMP-3.3; SOT230P696X180-4N
U5: ATSAMD21G-A; TQFP-48
U6: LM1117IMP-5.0; SOT230P696X180-4N
USB: USBMINIB; USB-MINIB
Y1: 32,768Khz_SMD; CRISTALLI_RESONATOR_EPSON_FC_145

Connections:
3V3: JP11.1, JP11.2
+3V3: C14.1, C38.1, C51.1, C52.1, IC10.5 (VDD), JP12.1, JP12.2, L4.2, R4.2, R57.2, R58.2, R62.2, U2.2 (VOUT), U2.4 (VOUT_2), U5.17 (VDDIO), U5.36 (VDDIO), U5.44 (VDDIN)
+5V: C13.1, JP5.4, JP6.2, JP10.1, JP10.2, R41.2, TR1.2 (S), U2.3 (VIN), U6.2 (VOUT), U6.4 (VOUT_2); also elsewhere on the board
+15V: C33.1, R60.2, U6.3 (VIN); also elsewhere on the board
DCLK: U5.23 (PA14(XIN/SER2:2+)); also elsewhere on the board
DCS: U5.24 (PA15(XOUT/SER2:3+)); also elsewhere on the board
DCURMON: U5.8 (PB09(AIN3/SER4:1/TC4:1))
DDATA: U5.22 (PA13(I2C/SER2:1+)); also elsewhere on the board
DGND: C11.2, C12.1, C13.2, C14.2, C23.2, C33.2, C38.2, C51.2, C52.2, C53.2, C54.2, C55.1, C56.1, IC10.3 (VSS), JP6.6, JP12.3, JP12.4, PWR.C, R59.1, R61.1, S1.1, U2.1 (ADJ/GND), U5.5 (GNDANA), U5.18 (GND), U5.35 (GND), U5.42 (GND), U6.1 (ADJ/GND), USB.GND; also elsewhere on the board
ENCA: U5.14 (PA09(I2C/AIN17/SER0:1+))
ENCB: U5.13 (PA08(I2C/AIN16/SER0:0+))
ENCBTN: U5.15 (PA10(AIN18/SER0:2+))
GND: H1.B2,8, H2.B2,8, H3.B2,8, H4.B2,8, JP5.5, JP10.3, JP10.4, JP11.3, JP11.4; also elsewhere on the board
unnamed: C54.1, L4.1, U5.6 (VDDANA)
unnamed: IC10.4 (O), R60.1, R61.2, TR1.3 (G)
unnamed: PWR.A, R41.1
unnamed: C55.2, U5.1 (PA00(XIN32/SER1:0/TC2:0)), Y1.P$2 (2)
unnamed: C56.2, U5.2 (PA01(XOUT32/SER1:1/TC2:1)), Y1.P$1 (1)
unnamed: JP14.3, U5.30 (PA21(SER5:3+))
unnamed: JP14.2, U5.29 (PA20(SER5:2+))
unnamed: JP14.1, U5.28 (PA19(SER1:3+))
PA02_AIN0: U5.3 (PA02(AIN0/DAC))
PA04_AIN4: JP13.2, U5.9 (PA04(AIN4/REFB/SER0:0/TC0:0))
PA05_AIN5: JP13.1, U5.10 (PA05(AIN5/SER0:1/TC0:1))
PA28_USB_HOST_EN: R63.1, U5.41 (PA28)
PB10_S4_SPI_MOSI: JP6.4, U5.19 (PB10(SER4:2+))
PB11_S4_SPI_SCK: JP6.3, U5.20 (PB11(SER4:3+))
PB12_S4_SPI_MISO: JP6.1, U5.21 (PA12(I2C/SER2:0+))
RESET: JP6.5, R4.1, R56.1, S1.3 (2)
RST: JP5.1
RXD: JP5.3
SCL: JP12.7, JP12.8, R58.1, U5.32 (PA23(I2C/SER3:0+))
SDA: JP12.5, JP12.6, R57.1, U5.31 (PA22(I2C/SER3:0+))
TARGET_RESET: C23.1, R56.2, U5.40 (!RESET!)
TARGET_USB_N: U5.33 (PA24(SER3:2+)), USB.D-
TARGET_USB_P: U5.34 (PA25(SER3:3+)), USB.D+
TXD: JP5.2
UGBIN: IC3.5 (+IN); also elsewhere on the board
UGBOUT: IC3.6 (-IN), IC3.7 (OUT)
USBVCC: C12.2, F1.2, R59.2, TR1.1 (D)
USB_ID: IC10.1 (OE), IC10.2 (I), R62.1, R63.2, USB.ID
V+: IC3.8 (V+)
V-: IC3.4 (V-)
VDDCORE: C53.1, U5.43 (VDDCORE)
VIN: U5.47 (PB02(AIN10/SER5:0))
XUSB: C11.1, F1.1, USB.VBUS

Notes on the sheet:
RST
TXD
RXD
+3V3
UGBIN
UGBOUT

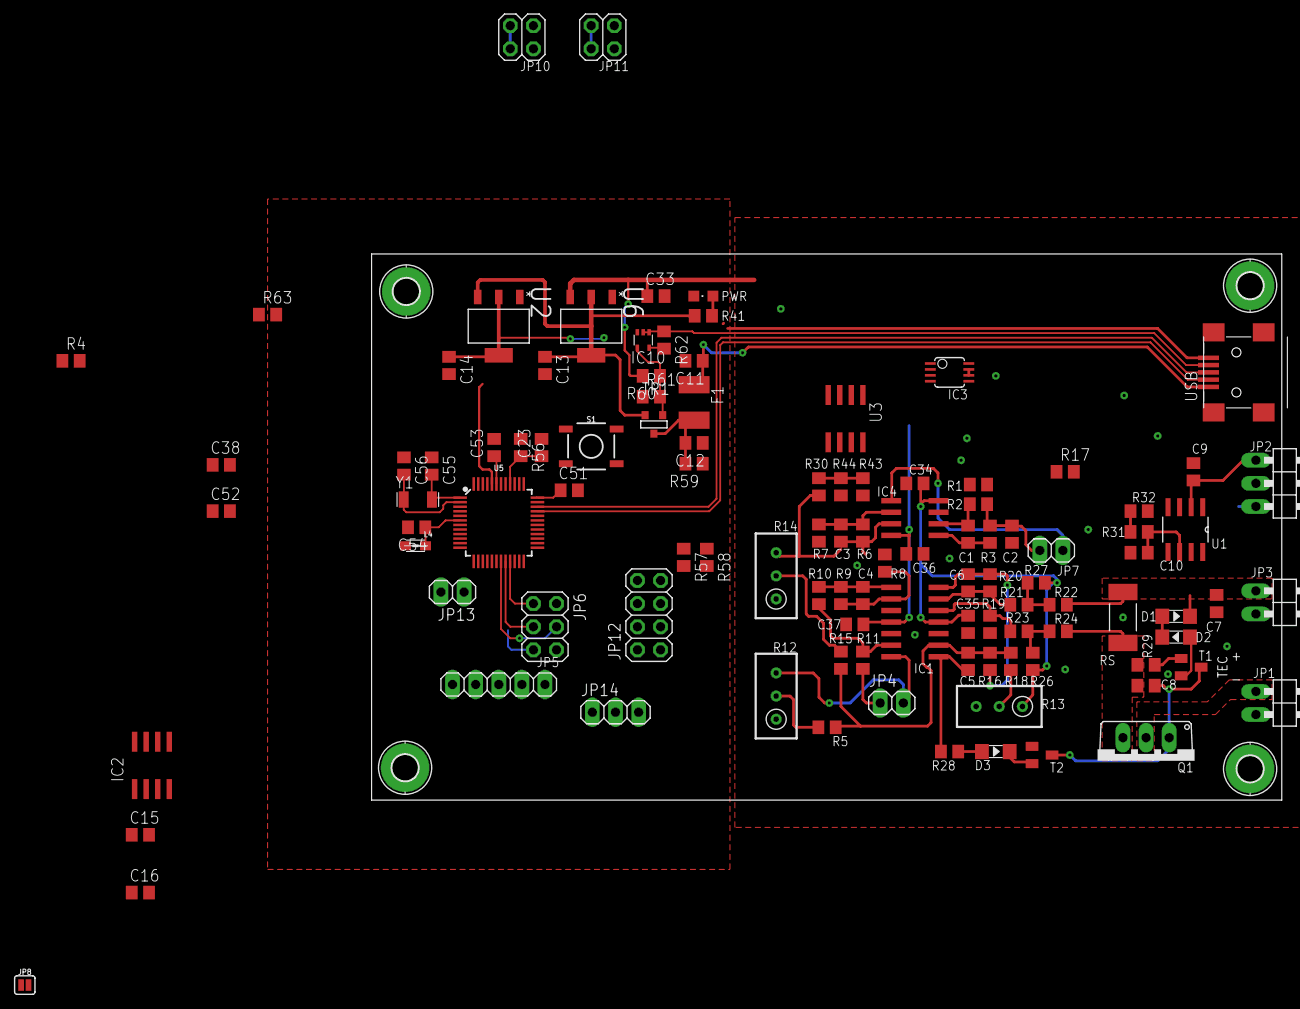
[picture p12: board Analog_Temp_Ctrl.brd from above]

Board: 2 copper layers, 100.0 x 60.0 mm, 112 parts (0 on the bottom side), 70 nets.

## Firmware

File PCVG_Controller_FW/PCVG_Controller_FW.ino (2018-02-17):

#include <SPI.h>
#include <Wire.h>
#include <Adafruit_SSD1306.h>
#include <stdlib.h>

#define OLED_RESET 4  //4
Adafruit_SSD1306 display(OLED_RESET);

const int ID_PIN = A4;
const int SIG_PIN = A3;

enum gaugeType {
  notFound,
  fulRangPirani, //idVal 981
  fulRangCombined, //idVal 819
  coldCathode //idVal 655
};

gaugeType curType = notFound;
float curPressure = 0;

//Setup routine
void setup() {

  pinMode(ID_PIN, INPUT);
  pinMode(SIG_PIN, INPUT);
  
  Serial.begin(115200);
  display.begin(SSD1306_SWITCHCAPVCC, 0x3C);
    
  // Clear the buffer.
  display.clearDisplay();
  display.display();

  display.setTextColor(WHITE);

}

//Read the voltage at the ID_PIN and set the current gauge type.
void identifyGauge() {
  int idVal = analogRead(ID_PIN);
  if ((idVal >= 500) && (idVal < 740)) {
    curType = coldCathode;
  }
  else if ((idVal >= 740) && (idVal < 900)) {
    curType = fulRangCombined;
  }
  else if (idVal >= 900) {
    curType = fulRangPirani;
  }
  else {
    curType = notFound;
  }
}

//Read the voltage at the SIG_PIN, average reading numAvgs times and convert it into a pressure using the formula provided in the datasheet.
void updatePressure() {

  float tmpReading = 0;
  int numAvgs = 50;

  for (int i=0; i < numAvgs; i++) {
    tmpReading += analogRead(SIG_PIN);
    delay(20);
  }

  float avgd = tmpReading / numAvgs; //average reading
  //Serial.println("AVG SIG VAL: " + String(avgd));
  float pressure = pow(10.00, 1.667*(avgd*21/2048)-11.33); //resistor divider and ADC resolution
  curPressure = pressure;

}

//Print the connected gauge type on the display.
void showGaugeType() {
  
  display.setTextSize(1);
  
  if (curType == notFound) {
    display.println("No Gauge found!");
  }
  else if (curType == fulRangPirani) {
    display.println("FRG - Pirani Only");
  }
  else if (curType == fulRangCombined) {
    display.println("FRG - Combined");
  }
  else {
    display.println("Cold Cathode Gauge");
  }

  display.display();
}

//Format the current pressure into a mantissa-exponent format and print it on the display.
char pString[10] = "";
void showPressureReading() {

  display.setTextSize(2);
  display.println("Pressure:");
  //display.println();
  
  display.setTextSize(2.5);
  dtostre(curPressure,pString,2,DTOSTR_ALWAYS_SIGN | DTOSTR_UPPERCASE);
  char *movedP = pString + 1;
  display.println(movedP);

  display.setTextSize(2);
  display.println("      mbar");
  display.display();
  
}

//Main worker loop
void loop() {

  display.clearDisplay();
  identifyGauge();
  updatePressure();

  display.setCursor(0,0);

  showGaugeType();
  showPressureReading();

  //OPT: If request code was received over serial interface, reply with current pressure.
  if (Serial.available() > 0) {
    int incomingByte;
    int index;
    incomingByte = Serial.read();
    index = incomingByte - 48;
    Serial.println(pString);
  }

  delay(50);
  

}

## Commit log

2017-12-03 Moved project files to GitHub. Revision 1.0.
    As manufactured in the first iteration.
    [ECDL_CUR_CTRL.GBL, ECDL_CUR_CTRL.GBO, ECDL_CUR_CTRL.GBS, ECDL_CUR_CTRL.GTL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]
2017-12-03 Added analog temperature controller.
    [Analog_Temp_Ctrl.brd, Analog_Temp_Ctrl.sch, ECDL_CUR_CTRL.sch]
2017-12-06 Completed Temperature Controller, Rdy for Mfg.
    [Analog_Temp_Ctrl.brd, Analog_Temp_Ctrl.sch]
2018-01-04 Preliminary changes to new version.
    New features: Microntroller for current driver as well, seperate A/D
    grounding, upgrade to ARM Cortec uC, several other improvements.
    [Analog_Temp_Ctrl.brd, Analog_Temp_Ctrl.sch, ECDL_CUR_CTRL.brd, ECDL_CUR_CTRL.sch]
2018-01-08 Rev1.1 of CUR CTRL Complete, Ready for Mfg. Temp Ctrl WIP
    [Analog_Temp_Ctrl.brd, Analog_Temp_Ctrl.sch, BOM.csv, ECDL_CUR_CTRL.GBL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]
2018-01-27 Added a Controller for the Pfeiffer IKR/PKR Series Compact Gauges. Temp Ctrl WIP...
    [Analog_Temp_Ctrl.brd, Analog_Temp_Ctrl.sch, BOM.csv, ECDL_CUR_CTRL.brd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]
2018-02-17 Added Pfeiffer G.auge Controller Schematics + FW
    [Analog_Temp_Ctrl.brd, Analog_Temp_Ctrl.sch, Pfeiffer_Compact_Gauge_Controller.GBL, Pfeiffer_Compact_Gauge_Controller.GBS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]
2018-03-27 Changes to Analog PID. Added LTC1923 Design.
    [Analog_PID_Controller.brd, Analog_PID_Controller.sch, ECDL_CUR_CTRL.brd, ECDL_CUR_CTRL.sch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]

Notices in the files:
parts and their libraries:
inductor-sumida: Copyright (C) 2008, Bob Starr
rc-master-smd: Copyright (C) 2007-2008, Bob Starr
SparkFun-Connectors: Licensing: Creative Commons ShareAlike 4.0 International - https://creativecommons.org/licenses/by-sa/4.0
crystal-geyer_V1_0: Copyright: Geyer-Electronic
